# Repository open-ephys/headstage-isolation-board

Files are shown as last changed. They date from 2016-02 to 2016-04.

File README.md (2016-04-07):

# headstage-isolation-board

## this design is not functional right now, see below

isolation board for RHD headstge, electrically decouples headstage from aq. board.
This could be useful for mitigating recording noise in some scenarious, or simplify proper grounding practive, especially if multiple recording rigs share the same acquisition board. Eventually, this device could be used to provide safety for human EEG or intracortical applications, but this would require extensive testing and approval procedures.

*This device has not been tested and is not considered safe for any use case. Only use this if you are approved to do so independently.*

# operating principle
This isolation board translates the LVDS signals to a single ended CMOS signal, isolates this signal and translates it back to LVDS. Power isolation is accomplished through a separate 5V isolation transformer.

## 2do:
change this to use the basic design form the FMC card at 
https://github.com/open-ephys/next-gen-system/tree/master/FMC-board

use only IEC60601-1 certified parts, this way we're on the safe side for US and EU standards
http://www.cui.com/catalog/resource/iec-60601-1-medical-design-standards.pdf

power DC-DC: http://www.digikey.com/en/product-highlight/r/recom-power/dcdc-converters
cmos isolation: http://www.analog.com/media/en/technical-documentation/data-sheets/ADuM4400_4401_4402.pdf

# old spec below

Based on Analog Devices ADUM3440 isolators 9 http://www.analog.com/media/en/technical-documentation/data-sheets/ADuM3440_3441_3442.pdf )
UL recognition: 2500 V rms for 1 minute per UL 1577,  CSA Component Acceptance Notice #5A, VDE certificate of conformity, DIN V VDE V 0884-10 (VDE V 0884-10):2006-12 
V_IORM = 560 V peak

LVDS<-> CMOS trsnalation is done via on Analog Devices ADN4664 Dual, 3 V, CMOS, LVDS Differential Line Receivers ( http://www.analog.com/media/en/technical-documentation/data-sheets/ADN4664.pdf ) and ADN4663 Dual, 3 V, CMOS, LVDS High Speed Differential Drivers ( http://www.analog.com/media/en/technical-documentation/data-sheets/ADN4663.pdf )

Power isolation is done with a Murata NMV0505 3kVDC Isolated 5V DC/DC Converters ( http://power.murata.com/data/power/ncl/kdc_nmv.pdf )

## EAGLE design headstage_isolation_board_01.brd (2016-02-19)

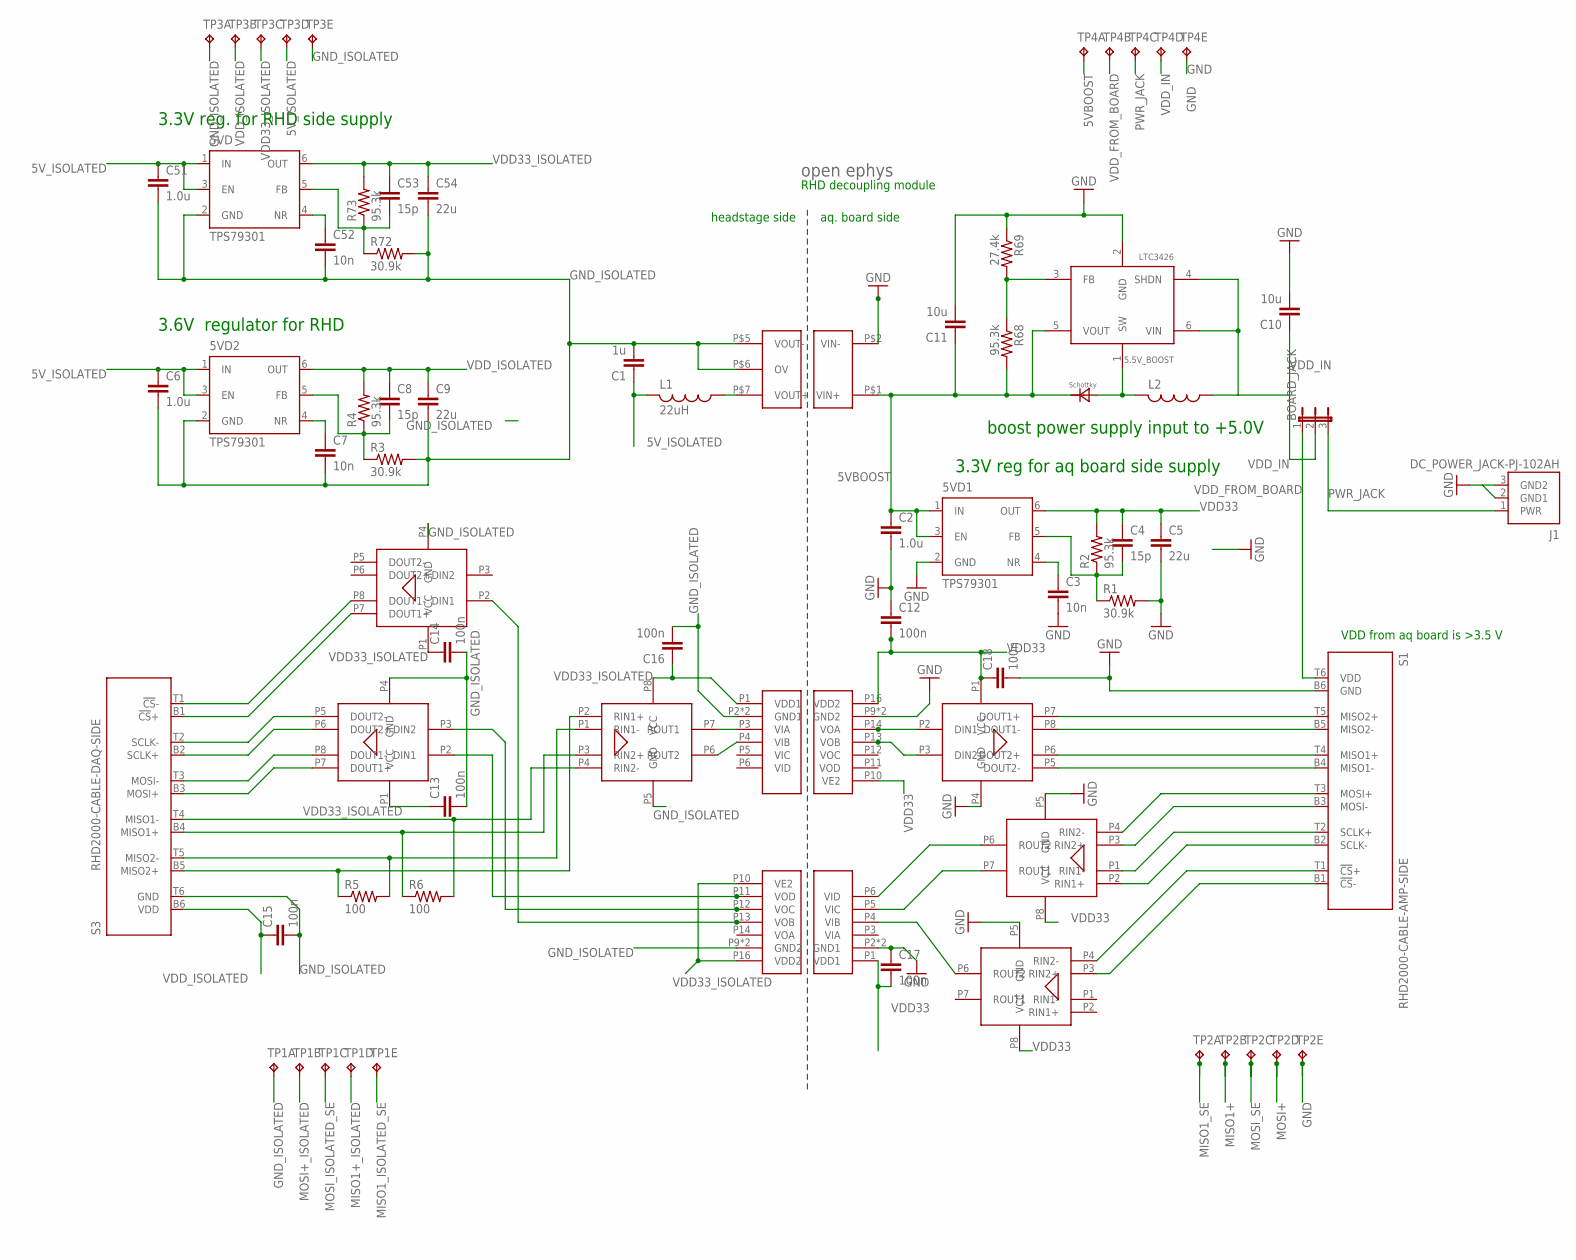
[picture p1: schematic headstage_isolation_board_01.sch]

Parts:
5.5V_BOOST: LTC3426; SOT23-6
5VD, 5VD1, 5VD2: TPS79301; SOT-23-6
BOARD_JACK: JP2E; JP2
C1: 1u; 1206
C2, C6, C51: 1.0u; 0805
C3, C7, C52: 10n; 0603
C4, C8, C53: 15p; 0603
C5, C9, C54: 22u; 1206
C10, C11: 10u; 1206
C12, C13, C14, C15, C16, C17, C18: 100n; 0603
D1: MBRA210LT3-D
J1: DC_POWER_JACK-PJ-102AH; PJ-102AH
L1: 22uH; 1206
L2: L_1206; 1206
R1, R3, R72: 30.9k; 0603
R2, R4, R68, R73: 95.3k; 0603
R5, R6: 100; 0603
R69: 27.4k; 0603
S1: RHD2000-CABLE-AMP-SIDE; OMNETICS_PZN-12-AA
S3: RHD2000-CABLE-DAQ-SIDE; OMNETICS_PZN-12-AA
TP1, TP2, TP3, TP4: TP5P5-25-13; P5-25-13
U$1: OPEN_EPHYS_LOGO
U$2, U$10: ADUM3440; SOIC_WIDE_16
U$4, U$5, U$9: ADN4663; 8-SOIC
U$6, U$7, U$8: ADN4664; 8-SOIC
U$12: NMV0505

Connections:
5VBOOST: 5.5V_BOOST.5 (VOUT), 5VD1.1 (IN), 5VD1.3 (EN), C2.1, C11.1, D1.NEG, R68.2, TP4.TP-1, U$12.P$1 (VIN+)
5V_ISOLATED: 5VD.1 (IN), 5VD.3 (EN), 5VD2.1 (IN), 5VD2.3 (EN), C1.1, C6.1, C51.1, L1.2, TP3.TP-4
CS+: S1.T1 (!CS!+), U$8.P4 (RIN2-)
CS+_ISOLATED: S3.B1 (!CS!+), U$9.P7 (DOUT1+)
CS-: S1.B1 (!CS!-), U$8.P3 (RIN2+)
CS-_ISOLATED: S3.T1 (!CS!-), U$9.P8 (DOUT1-)
CS_ISOLATED_SE: U$2.P13 (VOB), U$9.P2 (DIN1)
CS_SE: U$2.P4 (VIB), U$8.P6 (ROUT2)
GND: 5.5V_BOOST.2 (GND), 5VD1.2 (GND), C2.2, C3.2, C5.2, C10.2, C11.2, C12.1, C17.1, C18.2, J1.2 (GND1), J1.3 (GND2), R1.2, R69.1, S1.B6 (GND), TP2.TP-5, TP4.TP-5, U$2.P2 (GND1), U$2.P8 (GND1), U$4.P4 (GND), U$7.P5 (GND), U$8.P5 (GND), U$10.P9 (GND2), U$10.P15 (GND2), U$12.P$2 (VIN-)
GND4: C15.2
GND_ISOLATED: 5VD.2 (GND), 5VD2.2 (GND), C1.2, C6.2, C7.2, C9.2, C13.2, C14.2, C16.2, C51.2, C52.2, C54.2, R3.2, R72.2, S3.T6 (GND), TP1.TP-1, TP3.TP-1, TP3.TP-5, U$2.P9 (GND2), U$2.P15 (GND2), U$5.P4 (GND), U$6.P5 (GND), U$9.P4 (GND), U$10.P2 (GND1), U$10.P8 (GND1), U$12.P$5 (VOUT-), U$12.P$6 (OV)
MISO1+: S1.T4 (MISO1+), TP2.TP-2, U$4.P6 (DOUT2+)
MISO1+_ISOLATED: R6.1, S3.B4 (MISO1+), TP1.TP-4, U$6.P3 (RIN2+)
MISO1-: S1.B4 (MISO1-), U$4.P5 (DOUT2-)
MISO1-_ISOLATED: R6.2, S3.T4 (MISO1-), U$6.P4 (RIN2-)
MISO1_ISOLATED_SE: TP1.TP-5, U$6.P6 (ROUT2), U$10.P4 (VIB)
MISO1_SE: TP2.TP-1, U$4.P3 (DIN2), U$10.P13 (VOB)
MISO2+: S1.T5 (MISO2+), U$4.P7 (DOUT1+)
MISO2+_ISOLATED: R5.1, S3.B5 (MISO2+), U$6.P2 (RIN1+)
MISO2-: S1.B5 (MISO2-), U$4.P8 (DOUT1-)
MISO2-_ISOLATED: R5.2, S3.T5 (MISO2-), U$6.P1 (RIN1-)
MISO2_ISOLATED_SE: U$6.P7 (ROUT1), U$10.P3 (VIA)
MISO2_SE: U$4.P2 (DIN1), U$10.P14 (VOA)
MOSI+: S1.T3 (MOSI+), TP2.TP-4, U$7.P4 (RIN2-)
MOSI+_ISOLATED: S3.B3 (MOSI+), TP1.TP-2, U$5.P7 (DOUT1+)
MOSI-: S1.B3 (MOSI-), U$7.P3 (RIN2+)
MOSI-_ISOLATED: S3.T3 (MOSI-), U$5.P8 (DOUT1-)
MOSI_ISOLATED_SE: TP1.TP-3, U$2.P11 (VOD), U$5.P2 (DIN1)
MOSI_SE: TP2.TP-3, U$2.P6 (VID), U$7.P6 (ROUT2)
unnamed: L1.1, U$12.P$7 (VOUT+)
unnamed: 5VD1.4 (NR), C3.1
unnamed: 5VD1.5 (FB), C4.2, R1.1, R2.1
unnamed: 5VD2.4 (NR), C7.1
unnamed: 5VD2.5 (FB), C8.2, R3.1, R4.1
unnamed: 5VD.4 (NR), C52.1
unnamed: 5VD.5 (FB), C53.2, R72.1, R73.1
unnamed: 5.5V_BOOST.3 (FB), R68.1, R69.2
unnamed: 5.5V_BOOST.1 (SW), D1.POS, L2.2
PWR_JACK: BOARD_JACK.3, J1.1 (PWR), TP4.TP-3
SCLK+: S1.T2 (SCLK+), U$7.P1 (RIN1-)
SCLK+_ISOLATED: S3.B2 (SCLK+), U$5.P6 (DOUT2+)
SCLK-: S1.B2 (SCLK-), U$7.P2 (RIN1+)
SCLK-_ISOLATED: S3.T2 (SCLK-), U$5.P5 (DOUT2-)
SCLK_ISOLATED_SE: U$2.P12 (VOC), U$5.P3 (DIN2)
SCLK_SE: U$2.P5 (VIC), U$7.P7 (ROUT1)
VDD33: 5VD1.6 (OUT), C4.1, C5.1, C12.2, C17.2, C18.1, R2.2, U$2.P1 (VDD1), U$4.P1 (VCC), U$7.P8 (VCC), U$8.P8 (VCC), U$10.P10 (VE2), U$10.P16 (VDD2)
VDD33_ISOLATED: 5VD.6 (OUT), C13.1, C14.1, C16.1, C53.1, C54.1, R73.2, TP3.TP-3, U$2.P10 (VE2), U$2.P16 (VDD2), U$5.P1 (VCC), U$6.P8 (VCC), U$9.P1 (VCC), U$10.P1 (VDD1)
VDD_FROM_BOARD: BOARD_JACK.1, S1.T6 (VDD), TP4.TP-2
VDD_IN: 5.5V_BOOST.4 (SHDN), 5.5V_BOOST.6 (VIN), BOARD_JACK.2, C10.1, L2.1, TP4.TP-4
VDD_ISOLATED: 5VD2.6 (OUT), C8.1, C9.1, C15.1, R4.2, S3.B6 (VDD), TP3.TP-2

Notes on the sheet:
headstage side
aq. board side
VDD from aq board is >3.5 V
RHD decoupling module
boost power supply input to +5.0V
3.3V reg. for RHD side supply
3.3V reg for aq board side supply
3.6V regulator for RHD

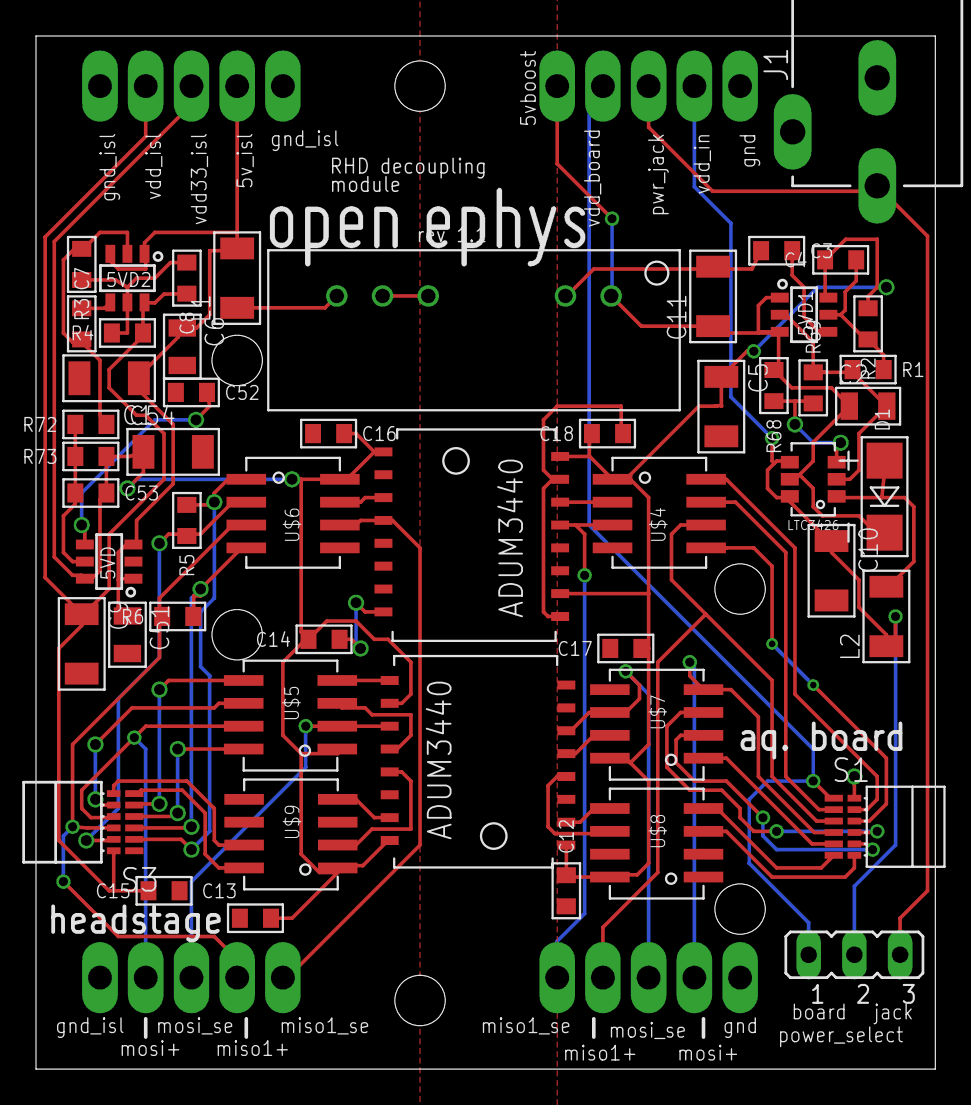
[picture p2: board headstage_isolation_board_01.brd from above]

Board: 2 copper layers, 50.0 x 57.4 mm, 57 parts (0 on the bottom side), 49 nets.

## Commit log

2013-11-19 initial commit
    pretty rough draft, completely lacks DC-DC converter
    [headstage_isolation_board_01.brd, headstage_isolation_board_01.sch]
2013-11-19 added DC-DC converter
    still missing resistors etc
    [headstage_isolation_board_01.brd, headstage_isolation_board_01.sch]
2013-11-19 initial partial layout, added some regulator parts
    still need to change r values for regulators
    [headstage_isolation_board_01.brd, headstage_isolation_board_01.sch]
2013-11-19 more layout of power side
    [headstage_isolation_board_01.brd]
2013-11-19 initial rough layout
    still missing correct resistor values
    [headstage_isolation_board_01.brd, headstage_isolation_board_01.sch]
2013-11-20 routing cleanup, added more bypass caps
    [headstage_isolation_board_01.brd, headstage_isolation_board_01.sch]
2013-12-02 Add gerber files
    [headstage_isolation_board_01.brd, headstage_isolation_board_01.drl]
2013-12-02 Add CAM file and update top silkscreen
    [headstage_isolation_board_01.brd]
2014-08-27 fix some naming CONNECTOR STILL WRONG- DONT USE YET
    [headstage_isolation_board_01.brd, headstage_isolation_board_01.sch]
2014-08-28 added correct connector
    [headstage_isolation_board_01.brd, headstage_isolation_board_01.sch]
2016-02-16 routed correct headstage connector
    and some other fixes.
    Still lacking testpoints
    [headstage_isolation_board_01.brd, headstage_isolation_board_01.sch]
2016-02-16 partially added test points/ dc jack
    can now choose between aq board power and external power jack, and
    added a few test points
    [headstage_isolation_board_01.brd, headstage_isolation_board_01.sch]
2016-02-16 added all test points
    [headstage_isolation_board_01.brd, headstage_isolation_board_01.sch]
2016-02-19 added LVDS termination resistors
    should fix bug #2
    [headstage_isolation_board_01.brd, headstage_isolation_board_01.sch]
2016-02-19 missing brd updates from last commit
    [headstage_isolation_board_01.brd]
